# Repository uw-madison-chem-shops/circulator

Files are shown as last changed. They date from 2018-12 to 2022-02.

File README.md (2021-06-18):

# circulator

Circulator for WiHP NMRR. 

coverart

## Repository

This is an open source hardware project licensed under the CERN Open Hardware License Version 2 - Permissive.
Please see the LICENSE file for the complete license.

This repository is being mirrored to several version control systems in an attempt to ensure maximum availability.

| name             | url                                                            |
| ---------------- | -------------------------------------------------------------- |
| Chem             | https://git.chem.wisc.edu/landis-group/WiHP-NMRR/circulator    |
| GitHub (primary) | https://github.com/uw-madison-chem-shops/circulator            |
| GitLab           | https://gitlab.com/uw-madison-chem-shops/circulator            |

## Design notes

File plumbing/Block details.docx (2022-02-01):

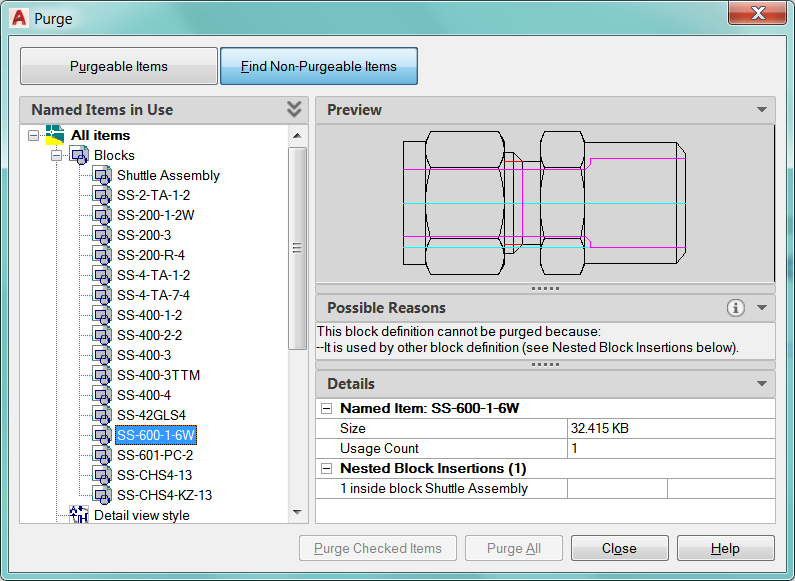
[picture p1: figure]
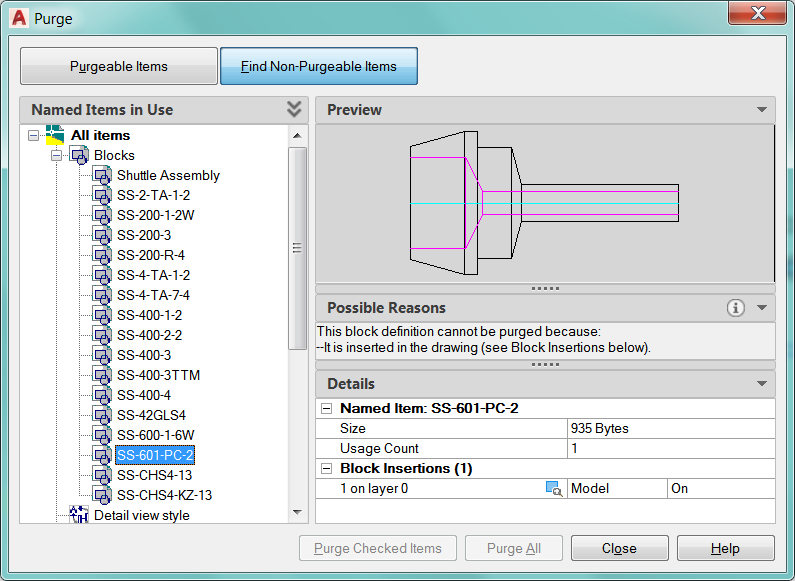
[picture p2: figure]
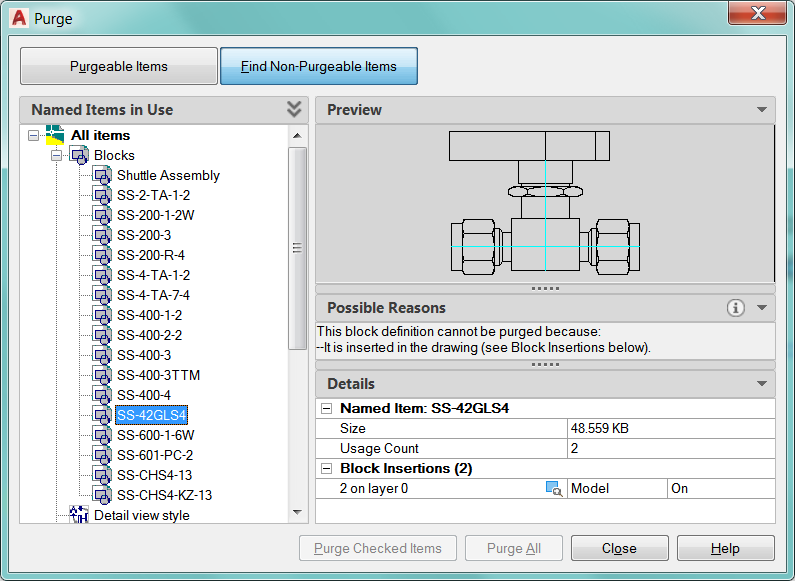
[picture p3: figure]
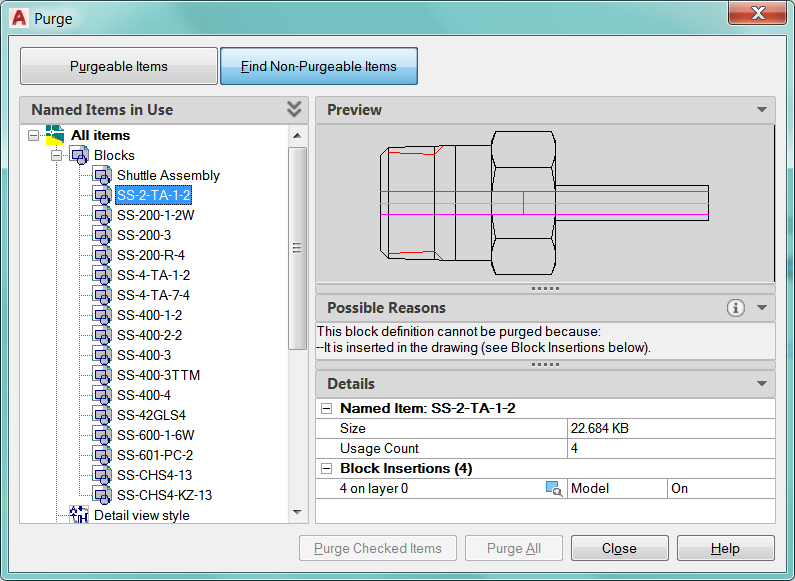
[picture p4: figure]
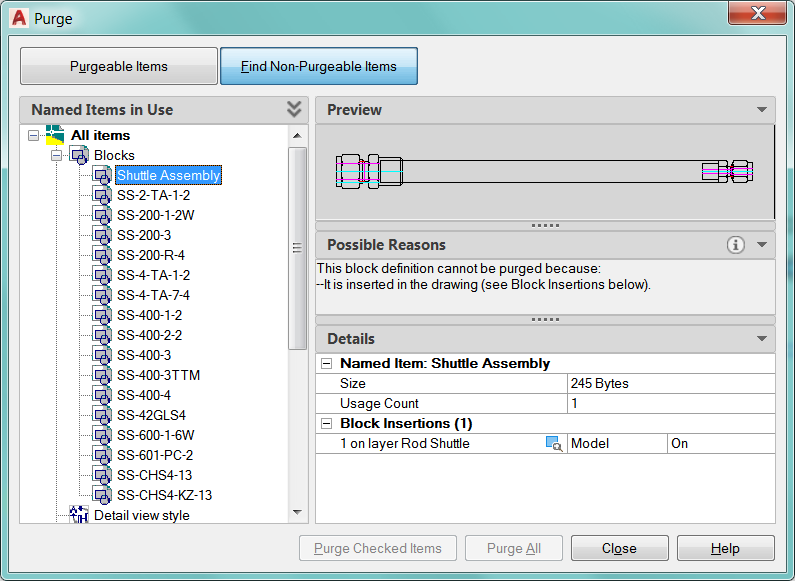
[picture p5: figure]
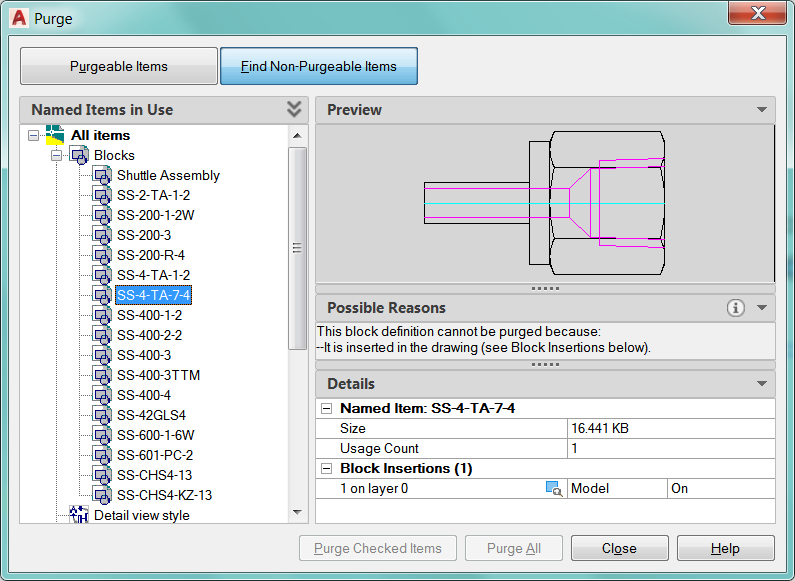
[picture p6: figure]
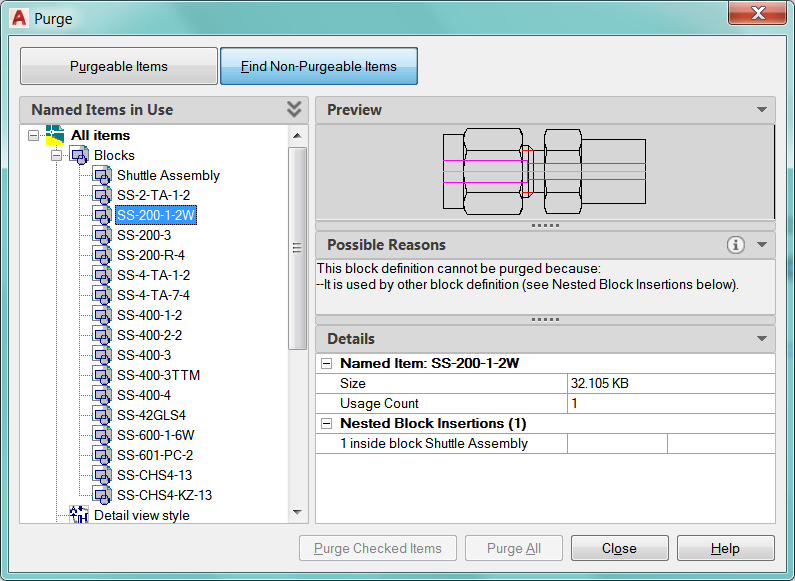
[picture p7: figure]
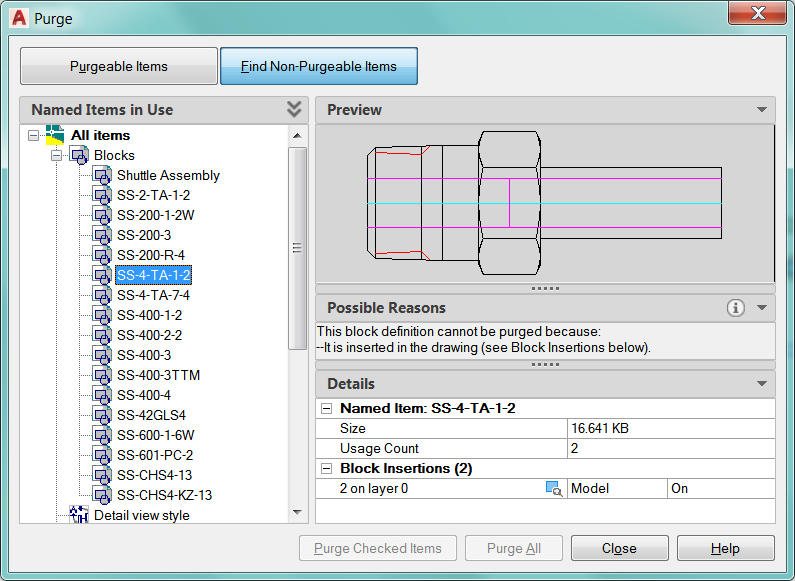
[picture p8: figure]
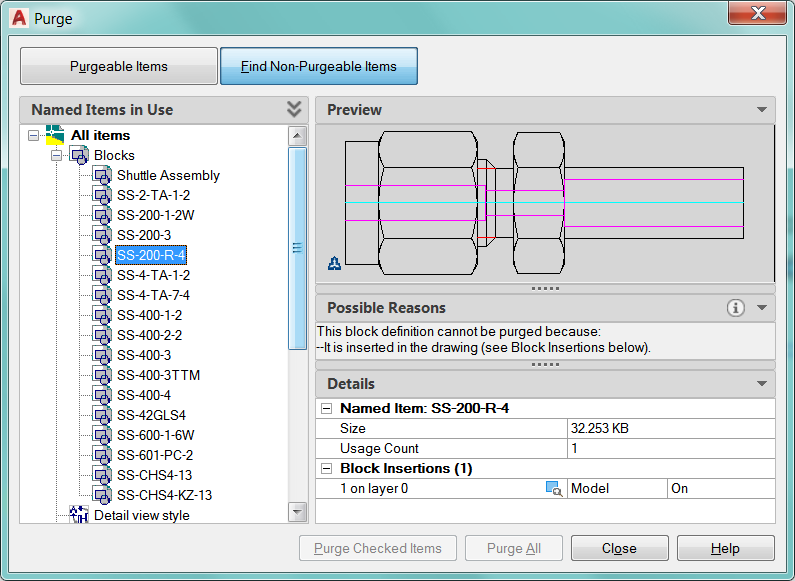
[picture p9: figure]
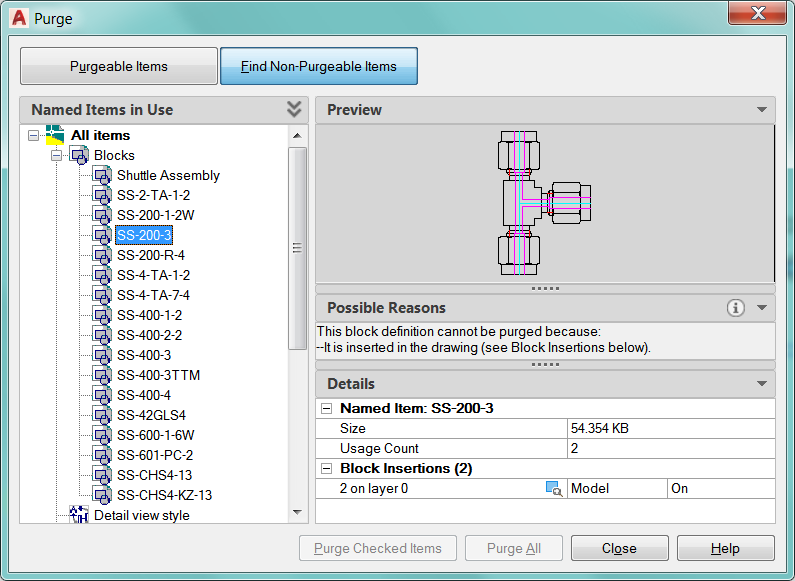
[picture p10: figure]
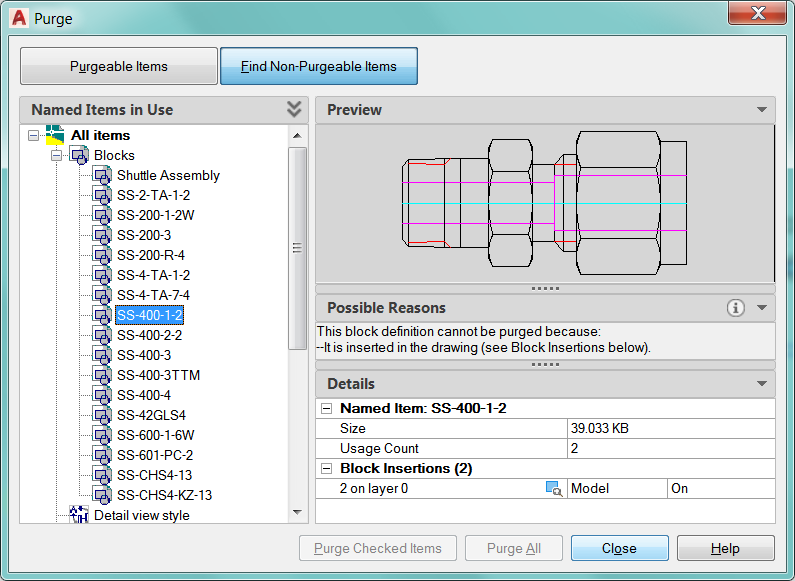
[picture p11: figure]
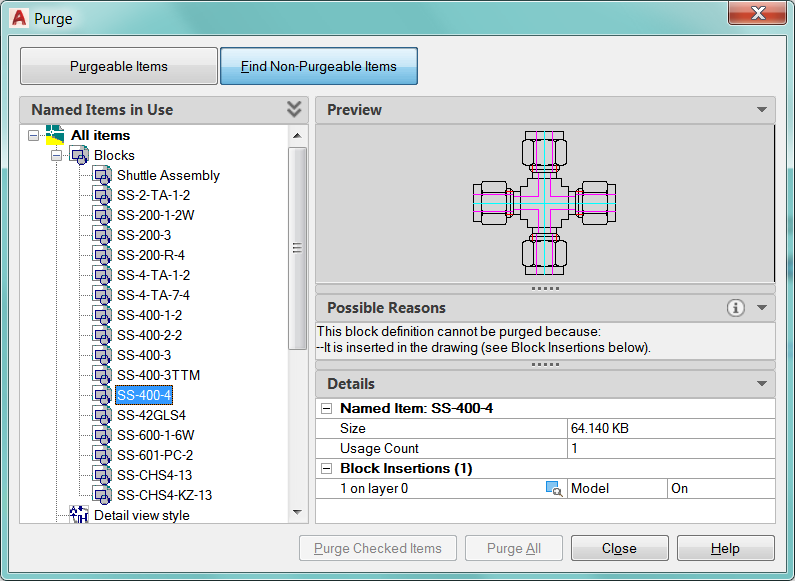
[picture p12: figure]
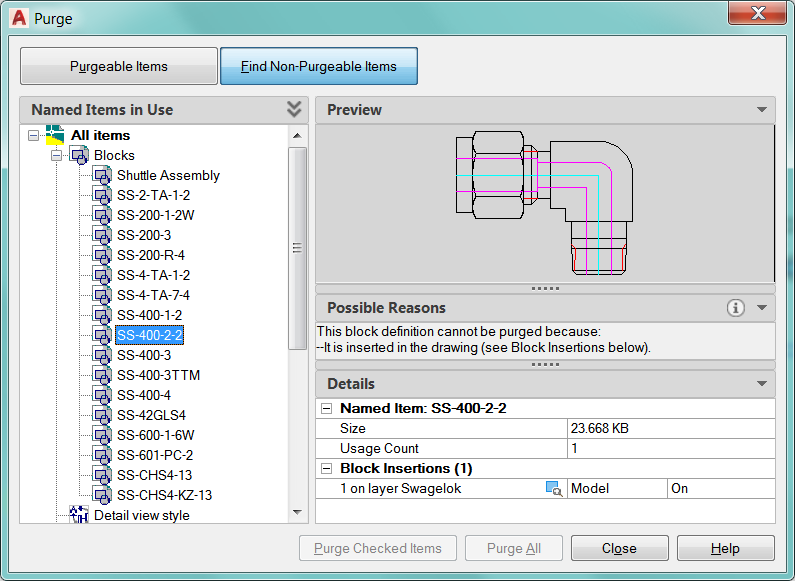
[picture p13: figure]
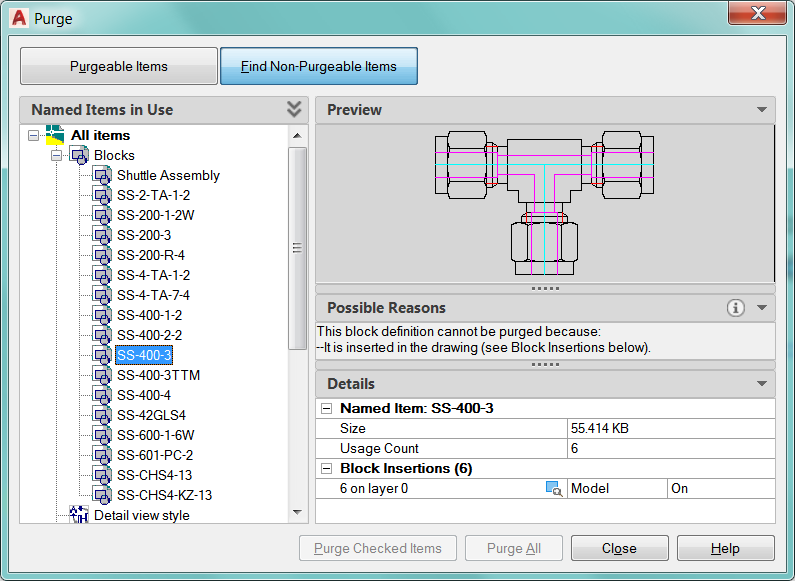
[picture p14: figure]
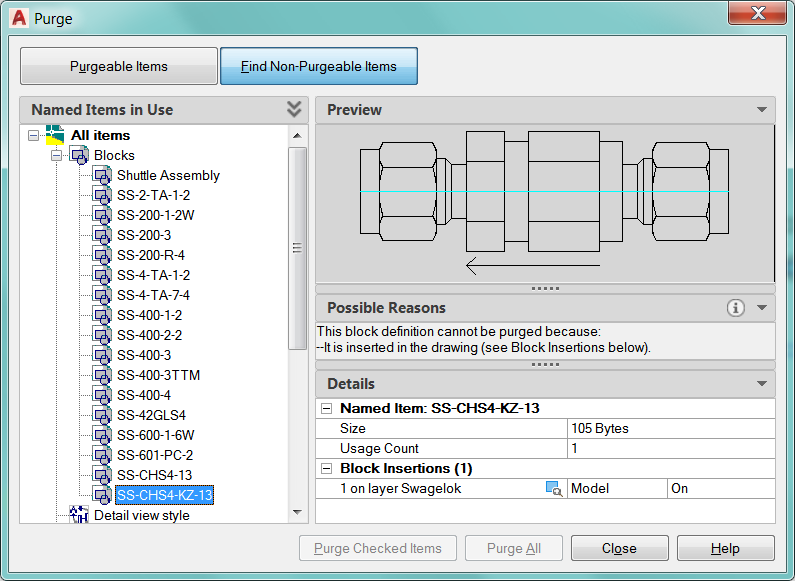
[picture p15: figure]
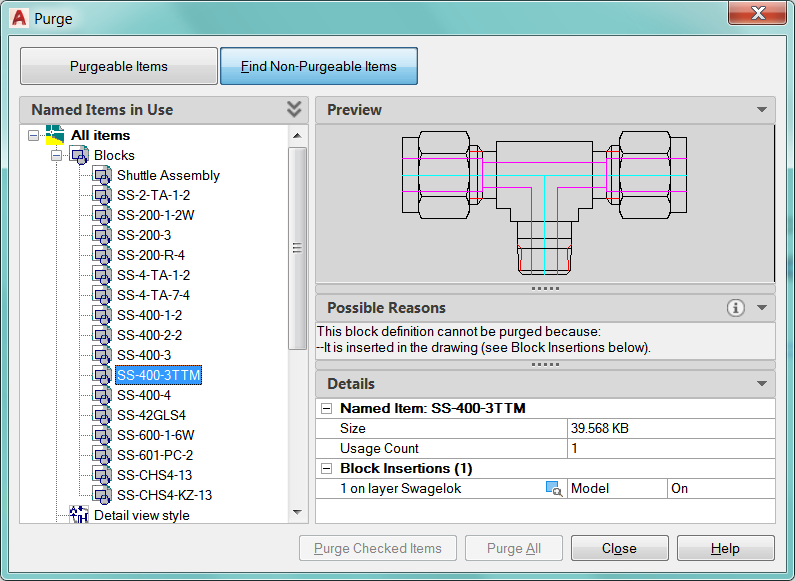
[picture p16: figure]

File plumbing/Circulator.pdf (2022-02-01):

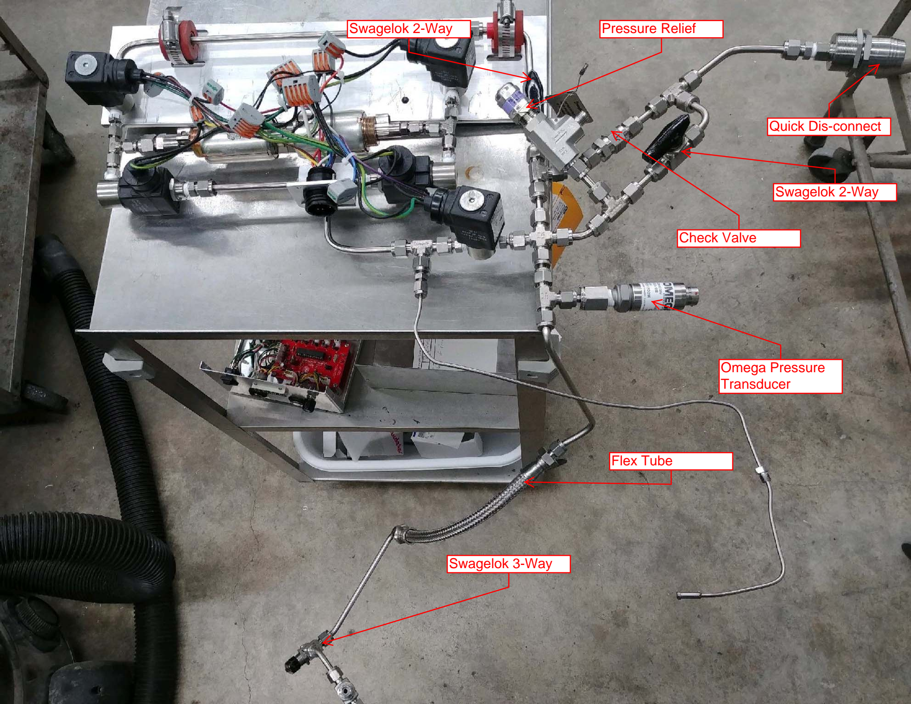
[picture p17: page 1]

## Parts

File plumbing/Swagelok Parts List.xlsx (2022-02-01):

Item | P/N | QTY. | Other
1 | SS-4-TA-7-4 | 1
2 | SS-200-1-2W | 1 | PART OF SHUTTLE
3 | SS-4-TA-1-2 | 2
4 | SHUTTLE ASSY. | 1
5 | SS-600-1-6W | 1 | PART OF SHUTTLE
6 | SS-42GLS4 | 2
7 | SS-601-PC-2 | 1
8 | SS-2-TA-1-2 | 4
9 | SS-200-R-4 | 1
10 | SS-400-1-2 | 2
11 | SS-200-3 | 2
12 | SS-400-4 | 1
13 | SS-400-2-2 | 1
14 | SS-CHS4-KZ-13 | 1
15 | SS-400-3 | 6
16 | SS-400-3TTM | 1

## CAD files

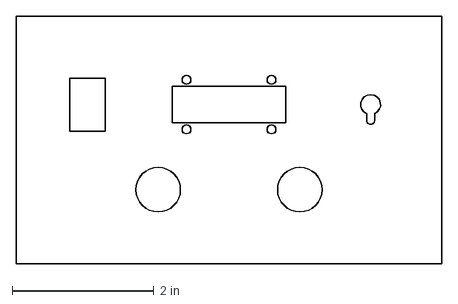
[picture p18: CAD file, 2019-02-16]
enclosure/front.dxf
6.00 x 3.50 in

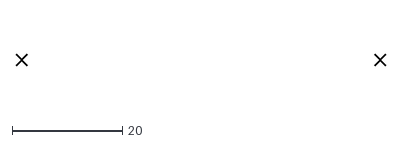
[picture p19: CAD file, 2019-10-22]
literature/power_supply.dxf
67.0 x 2.00

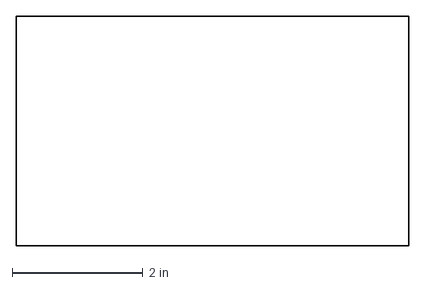
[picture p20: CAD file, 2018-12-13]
enclosure/back.dxf
6.00 x 3.50 in

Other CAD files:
plumbing/Rod Shuttle Assy.dwg
plumbing/Short rod bumper.dwg
plumbing/Circulator_Schem_copy.dwg

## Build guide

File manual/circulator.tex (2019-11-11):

\documentclass{manual}
\pagenumbering{gobble}

\usepackage{listings}

\title{circulator}

\begin{document}

\maketitle

\vspace*{\fill}
\begin{center}
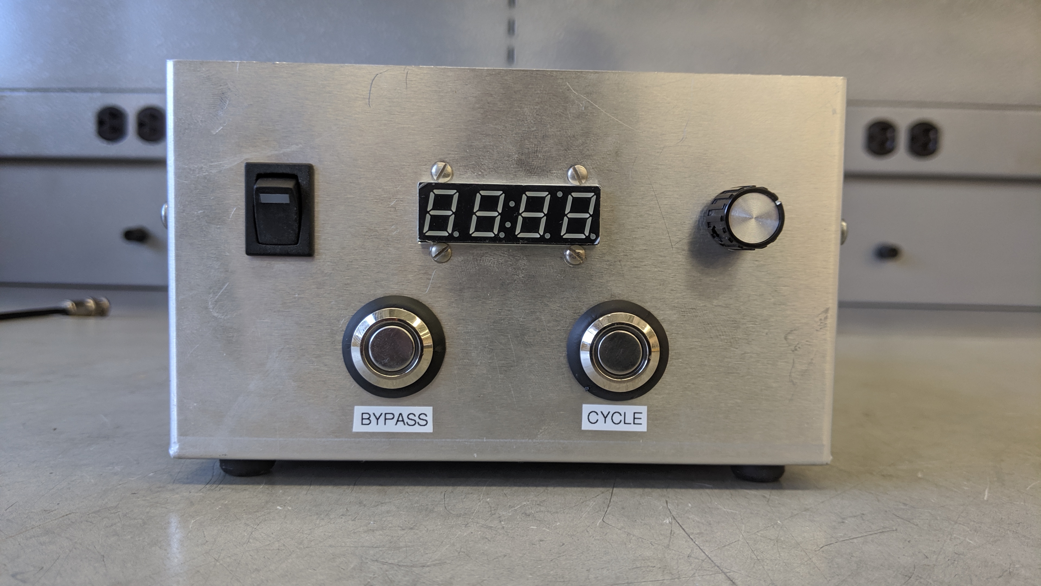
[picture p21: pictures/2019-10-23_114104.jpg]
  
\end{center}
\vspace*{\fill}

\section{description}
\pagenumbering{arabic}

The circulator is responsible for mass transport within the WiHP-NMRR.
It consists of five solenoid valves, and two core solenoids that drive a central piston.
These fire in a certain pattern to drive gas through the WiHP-NMRR.

The circulator driver is an box of electronics that drive the seven solenoids.

\section{solenoids, cable}

\begin{center}
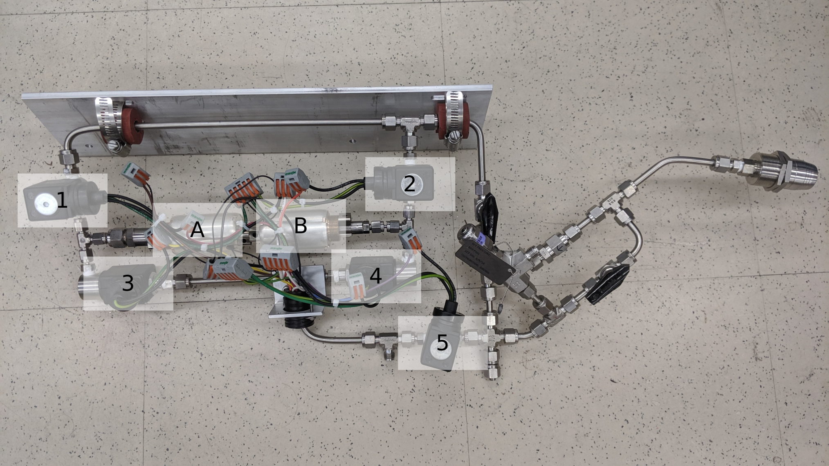
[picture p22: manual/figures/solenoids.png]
  
\end{center}

The image above shows the circulator itself, with the five solenoid valves and two piston solenoids labeled.
The valves are labeled with numbers, one through five.
The piston drivers are labeled with letters, A and B.
This convention is maintained throughout this document.

Valves 1, 2 and 5 are normally closed.
Valves 3 and 4 are normally open.
The following pattern must be followed to circulate:

\begin{table}[h]
\begin{tabular}{l|ll}
  & "tick" & "tock" \\ \hline
A & energized & denergized \\
2 & energized (open) & denergized (closed) \\
4 & energized (closed) & denergized (open) \\
B & denergized & energized \\
1 & denergized (closed) & energized (open) \\
3 & denergized (open) & energized (closed)
\end{tabular}
\end{table}

On the ``tick'' step, the piston moves from B to A, pulling gas through valve 2 and pushing gas out through valve 3.
On the ``tock'' step, the piston moves from A to B, pulling gas through valve 1 and pushing gas out through valve 4.

Valve five bypasses the circulator, and is operated separately from the rest of the solenoids.
The circulator is bypassed when valve five is energized.

\clearpage

Electrically, the five valves all operate on 120 V AC.
The two piston solenoids operate at 12 V DC.
Each of the components has a separate wire controlling line (or positive) voltage within the cable.
The components share ground and neutral.
The piston solenoids are ground referenced.

The circulator is connected by a circular plastic connector, TE/AMP part numbers 206037-1 and 206036-1.
The pin designations are as follows.

\begin{table}[h]
\begin{tabular}{l|ll}
pin & color & assignment \\ \hline
1 & white & neutral \\
2 & red & valve 1 \\
3 & orange & valve 2 \\
4 & yellow & valve 3 \\
5 & blue & valve 4 \\
6 & purple & valve 5 \\
7 & & \\
8 & & \\
9 & & \\
10 & & \\
11 & & \\
12 & & \\
13 & & \\
14 & green & ground \\
15 & brown & solenoid A \\
16 & black & solenoid B
\end{tabular}
\end{table}

\section{electrical box}

\begin{center}
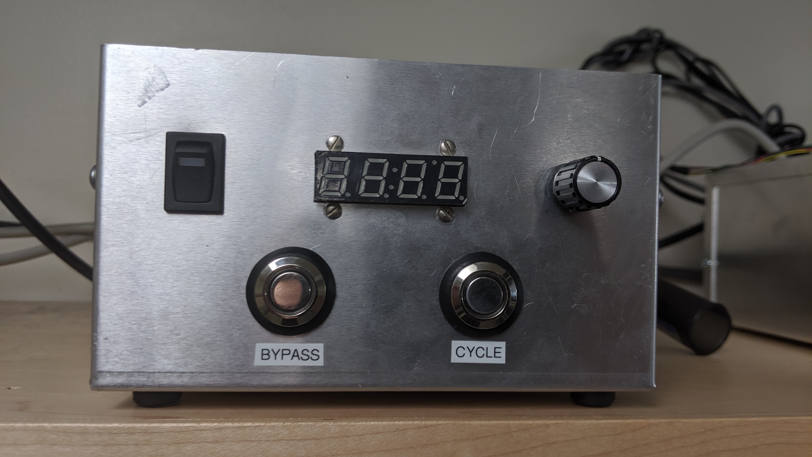
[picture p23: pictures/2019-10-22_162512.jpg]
  
\end{center}

The circulator driver controls the firing of the valves and solenoids necessary for mass transport in the WiHP-NMRR.
The image above is the front of the circulator driver box.
There is a power switch, far left.
The seven segment display in the middle shows the current circulator frequency, in Hz.
This frequency can be adjusted using the encoder knob, right.
Two buttons, one for bypass and the other for cycle, control the current status of the circulator.
Mechanically these are toggle buttons, and each toggles their corresponding state.
Each button contains an illuminated ring which will always display the current state.
These states can also be updated via TTL, as will be discussed later.

\begin{center}
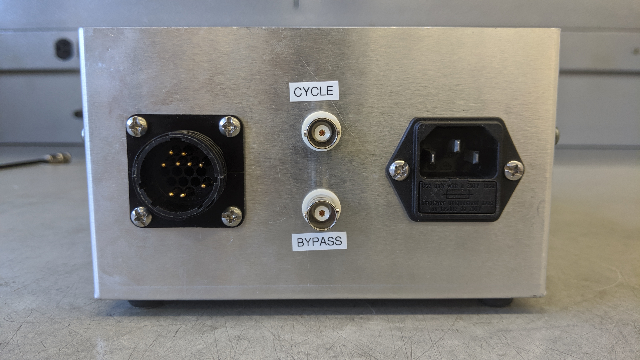
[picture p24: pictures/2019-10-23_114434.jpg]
  
\end{center}

The image above shows the rear of the circulator driver box.
There is a sixteen-pin CPC connector, left, which goes to the circulator itself.
In the middle there are two BNC inputs, cycle and bypass, which accept TTL control from the NMR.
On the right there is power input, which accepts a standard C13 connector.
The circulator operates at 120 V, and may draw up to 5 amps.
There is a fuse within the drawer immediately under the AC entry port.

\clearpage

\begin{center}
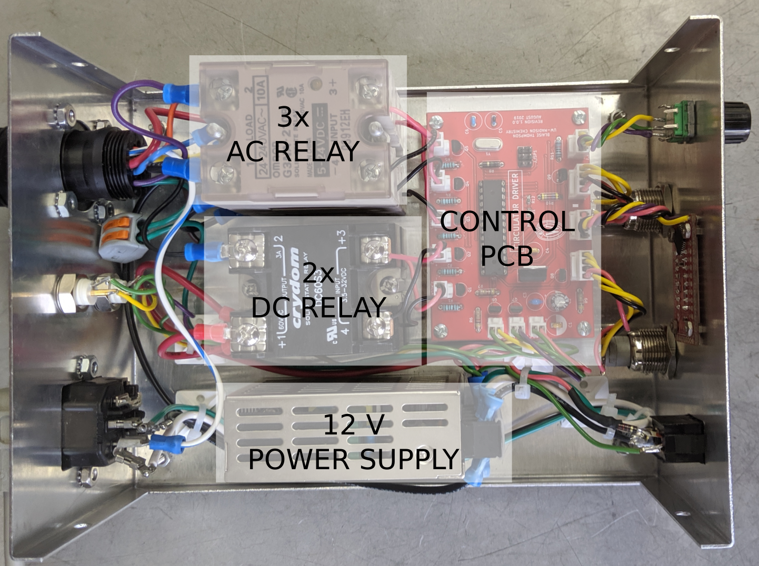
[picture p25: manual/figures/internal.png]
  
\end{center}

The image above shows the internals of the circulator driver box.
The enclosure used is 8'' x 6'' by 3.5'', Bud Industries part number CU-3009-A.
Besides the front and back panel elements, the box contains a 12 V power supply (TRACO part number  TXL 025-12S), 2 DC relays (Crydom part number DC60S3), and 3 AC relays (Omron part number G3NA-205B).
The relays and power supply make up the majority of the cost of the drive electronics.

Also contained within the enclosure is the custom control printed circuit board (PCB).
This central control board accepts power from the 12 V supply, input from the two rear-panel BNC connectors, and connects to the front panel elements and five relays.
At the core of the control board is a microcontroller with custom firmware.
These will all be discussed in the next few sections of this manual.

\section{circuit board}

\begin{center}
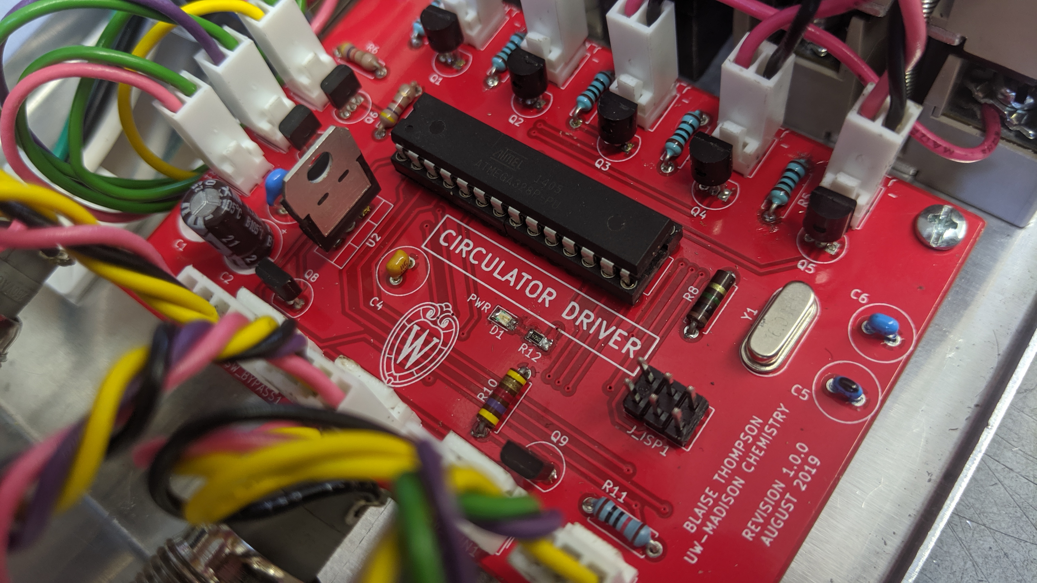
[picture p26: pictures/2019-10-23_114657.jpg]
  
\end{center}

The following pages diagram the printed circuit board (PCB) at the heart of the circulator driver electronics.
This PCB is centered around a single microcontroller, the ATmega328.
A 16 MHz crystal supplies the clock for the microcontroller.
A standard six pin ISP header can be used to program the microcontroller in-circuit.

The microcontroller has outputs to drive five relays, each controlling the action of a small NPN transistor (2N7000) with an appropriate pull-up resistor.
These five relays drive the circulator solenoids, as described in the previous section.
The microcontroller has two TTL inputs, each buffered by a small PNP transistor (BS250) and associated pull-down resistor.

Besides these, the microcontroller has inputs for the two front-panel buttons and the front-panel encoder.
There are also outputs for the LEDs embedded within each front-panel button, and for the seven-segment display (SparkFun part number COM-11441) (driven via I2C).

The following pages contain:
\begin{enumerate}
  \item PCB schematic
  \item PCB silk screen
  \item PCB top copper layer
  \item PCB bottom copper layer
\end{enumerate}
Please note that PCB silk screen and copper representations are to-scale.

The next sections describe the microcontroller firmware and PCB components.

\includepdf[angle=0, fitpaper=true]{../PCB/pcb.pdf}
\includepdf[angle=0, fitpaper=true]{../PCB/silk.pdf}
\includepdf[angle=0, fitpaper=true]{../PCB/front.pdf}
\includepdf[angle=0, fitpaper=true]{../PCB/back.pdf}

\section{firmware}

The following pages contain the raw source-code running on the embedded Atmega328 microcontroller.

\vspace{10pt}
\hrule

\lstinputlisting[language=c++]{../firmware/firmware.ino}

\section{BOM}

The following is an INCOMPLETE bill of materials for the circulator.
Trivial components like screws and resistors have been excluded.

\begin{tabular}{lrrrrl}
item & part & rate & count & total & comment\\
\hline
AC relay & G3NA-205B & 27.00 & 3 & 81.00 & \\
DC relay & DC60S3 & 21.00 & 2 & 42.00 & \\
12 V power supply & TXL 025-12S & 37.00 & 1 & 37.00 & \\
enclosure & CU-3009-A & 16.00 & 1 & 16.00 & \\
CPC pin & 66103-4 & 0.75 & 20 & 15.00 & \\
CPC socket & 1-66105-9 & 0.75 & 20 & 15.00 & \\
CPC plug & 206037-1 & 6.00 & 2 & 12.00 & \\
CPC socket & 206036-1 & 5.00 & 2 & 10.00 & \\
BNC jack & 031-10-RFXG1 & 3.00 & 2 & 6.00 & \\
AC entry & 6200-2300 & 6.00 & 1 & 5.00 & \\
16 MHz xtal & HC-49/U-S16000000ABJB & 1.00 & 1 & 1.00 & \\
header, 2 pin & 22-23-2021 & 0.25 & 8 & 2.00 & \\
header, 4 pin & 22-23-2041 & 0.50 & 3 & 1.50 & \\
header, 3 pin & 22-23-2031 & 0.25 & 1 & 0.25 & \\
DIP socket, 14 pin & 110-93-314-41-0010000 & 1.50 & 2 & 3.00 & \\
housing, 2 pin & 22-01-3027 & 0.25 & 8 & 2.00 & \\
housing, 3 pin & 22-01-3037 & 0.50 & 1 & 0.50 & \\
mosfet, N-channel & 2N7000 & 0.25 & 5 & 1.25 & \\
fuse, 1 A fast &  & 1.00 & 2 & 2.00 & \\
ring terminal, \#6, 14-16 AWG & 34158 & 0.50 & 10 & 5.00 & \\
capacitor, 33 nF & FG14X7R1H334KNT06 & 0.25 & 1 & 0.25 & \\
standoff, 0.5" \#4-40 &  & 0.50 & 4 & 2.00 & \\
housing, 4 pin & 22-01-3047 & 0.50 & 3 & 1.50 & \\
capacitor, 100 uF &  & 0.25 & 1 & 0.25 & \\
regulator, 5 V & 7805 & 1.00 & 1 & 1.00 & \\
switch & R1966ABLKBLKEFGRN & 2.00 & 1 & 2.00 & \\
7 segment display & COM-11441 & 15.00 & 1 & 15.00 & \\
rotary encoder & EN11 & 1.50 & 1 & 1.50 & \\
button, illuminated &  & 2.00 & 2 & 4.00 & \\
terminal block, 2 contact & 222-412 & 0.50 & 8 & 4.00 & \\
terminal block, 3 contact & 222-413 & 0.50 & 2 & 1.00 & \\
terminal block, 5 contact & 222-415 & 0.75 & 3 & 2.25 & \\
rubber bumper & 720 & 0.25 & 4 & 1.00 & \\
\end{tabular}

\end{document}

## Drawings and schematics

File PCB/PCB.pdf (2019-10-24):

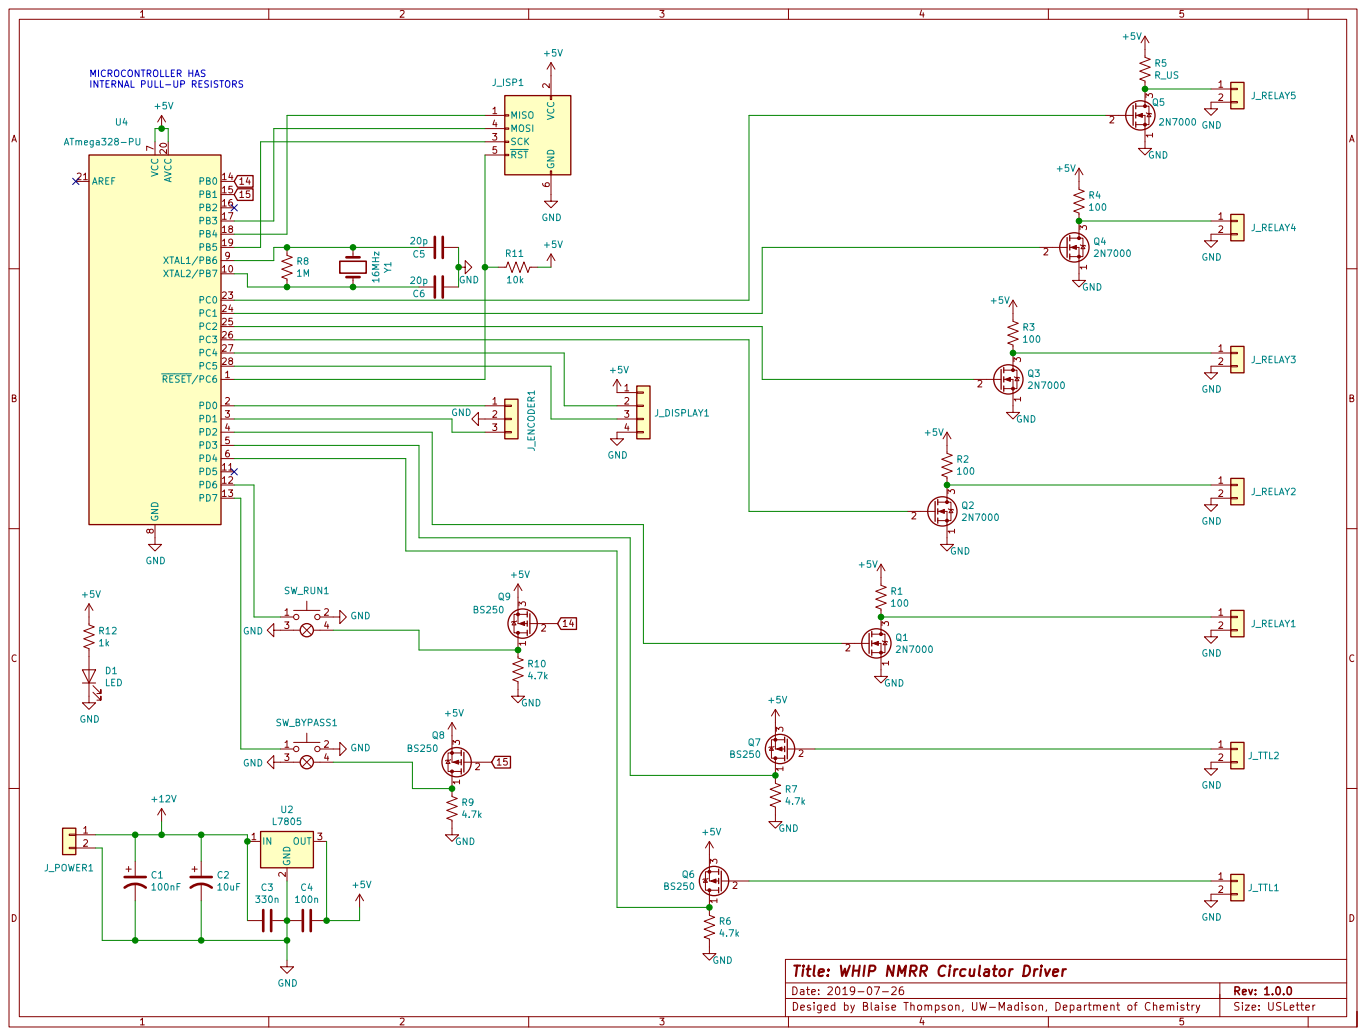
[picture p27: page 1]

14 MICROCONTROLLER HAS
INTERNAL PULL-UP RESISTORS

2 SCK 3 MOSI 4 RST 5 GND

Desiged by Blaise Thompson, UW-Madison, Department of Chemistry

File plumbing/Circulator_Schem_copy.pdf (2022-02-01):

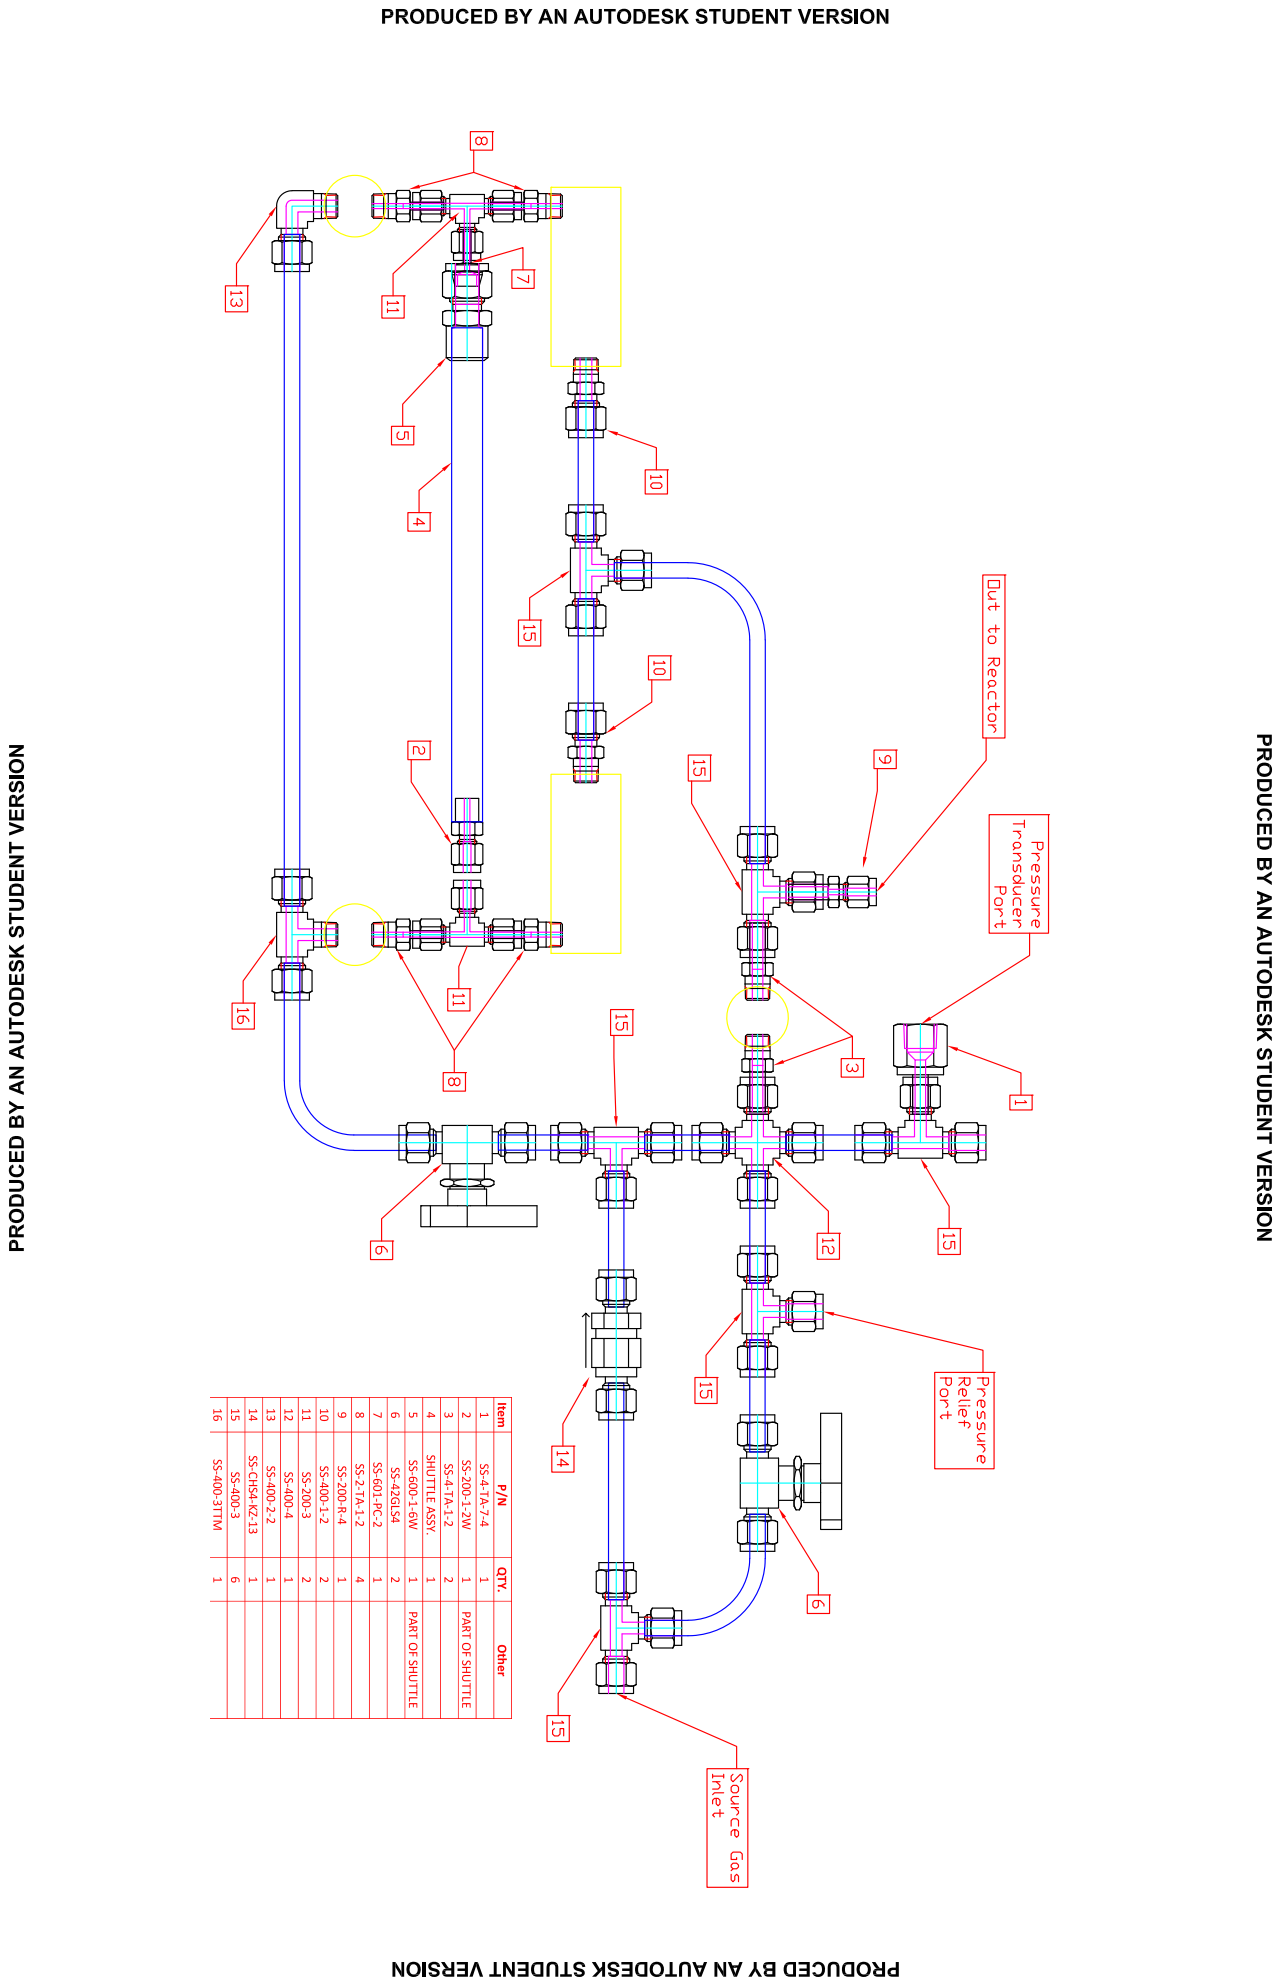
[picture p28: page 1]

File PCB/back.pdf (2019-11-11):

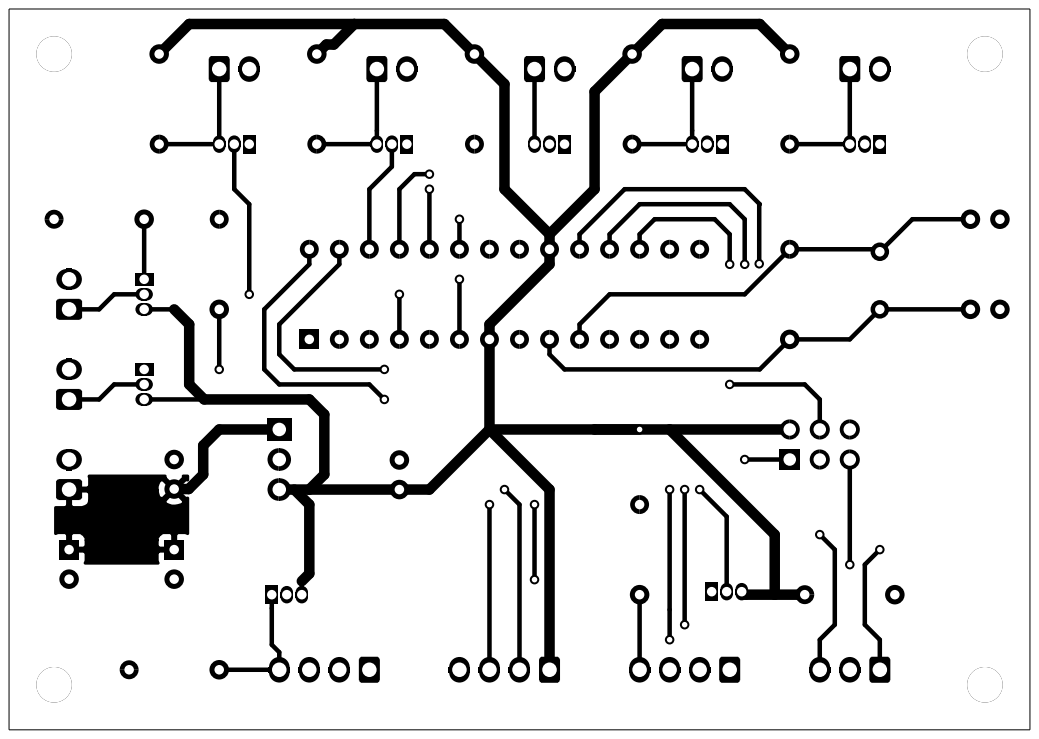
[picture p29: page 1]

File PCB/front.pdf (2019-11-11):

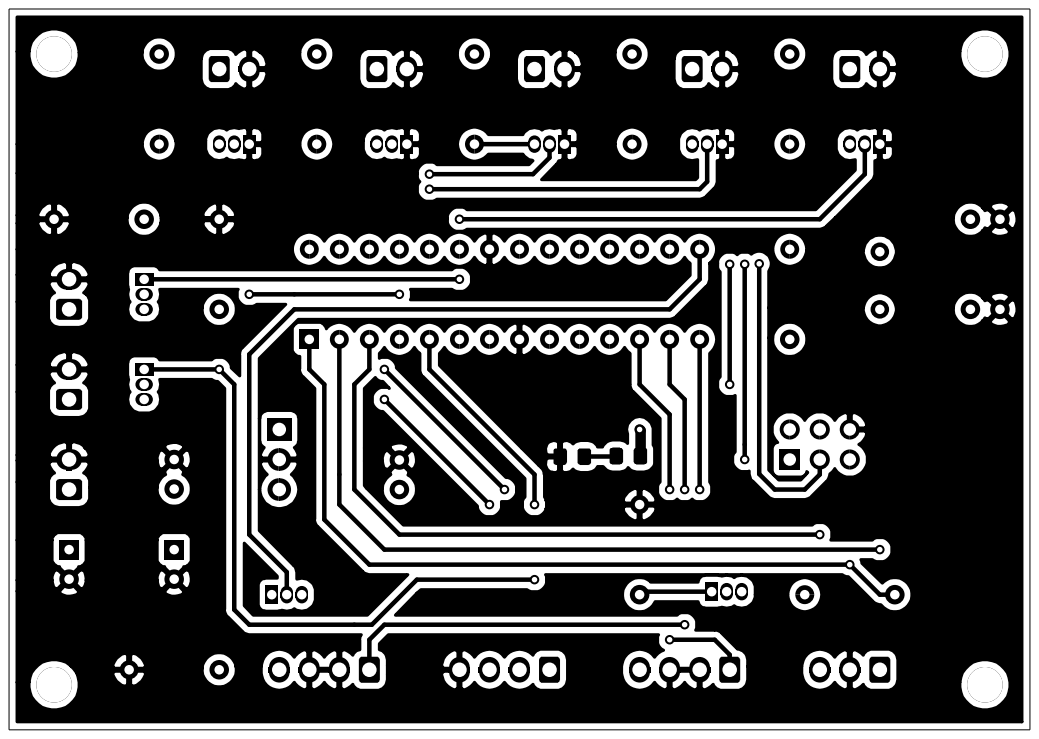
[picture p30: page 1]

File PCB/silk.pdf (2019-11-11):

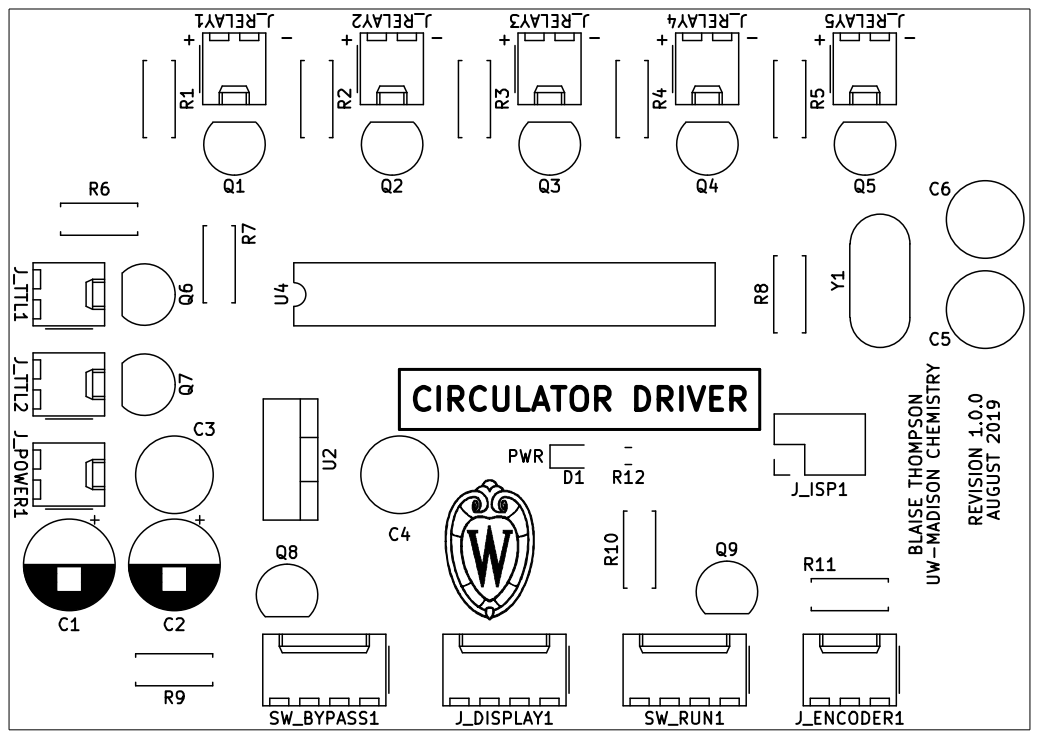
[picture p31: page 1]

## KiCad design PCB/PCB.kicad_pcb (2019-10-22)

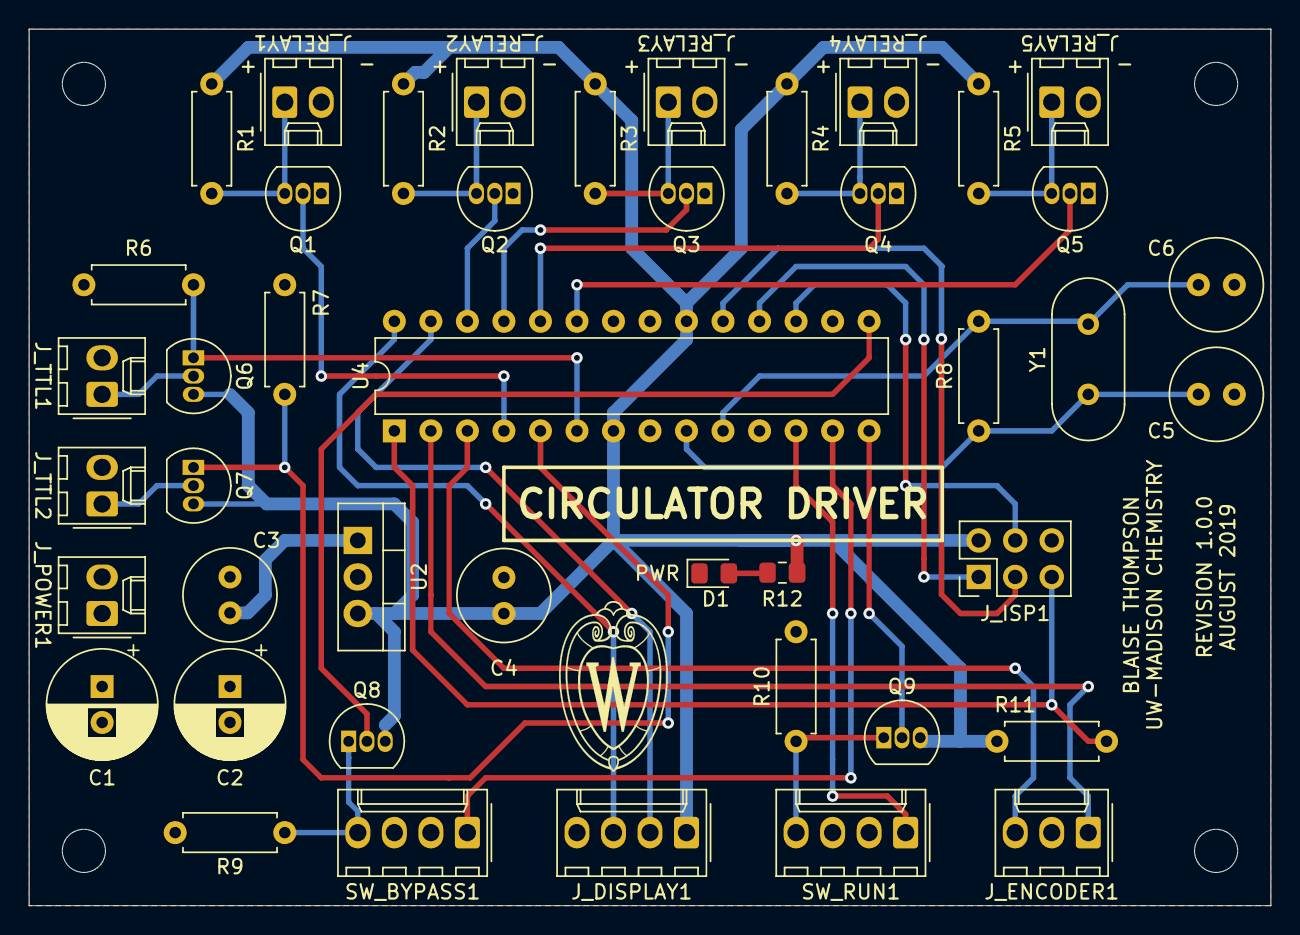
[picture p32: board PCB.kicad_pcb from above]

Board: 2 copper layers, 86.4 x 61.0 mm, 44 parts (0 on the bottom side), 34 nets.

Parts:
C1: 100nF; CP_Radial_D7.5mm_P2.50mm
C2: 10uF; CP_Radial_D7.5mm_P2.50mm
C3: 330n; C_Radial_D6.3mm_H5.0mm_P2.50mm
C4: 100n; C_Radial_D6.3mm_H5.0mm_P2.50mm
C5, C6: 20p; C_Radial_D6.3mm_H5.0mm_P2.50mm
D1: LED; D_0805_2012Metric_Pad1.15x1.40mm_HandSolder
J_DISPLAY1: Conn_01x04; Molex_KK-254_AE-6410-04A_1x04_P2.54mm_Vertical
J_ENCODER1: Conn_01x03; Molex_KK-254_AE-6410-03A_1x03_P2.54mm_Vertical
J_ISP1: AVR-ISP-6; PinHeader_2x03_P2.54mm_Vertical
J_POWER1: Conn_01x02; Molex_KK-254_AE-6410-02A_1x02_P2.54mm_Vertical
J_RELAY1, J_RELAY2, J_RELAY3, J_RELAY4, J_RELAY5: Conn_01x02; Molex_KK-254_AE-6410-02A_1x02_P2.54mm_Vertical
J_TTL1, J_TTL2: Conn_01x02; Molex_KK-254_AE-6410-02A_1x02_P2.54mm_Vertical
Q1, Q2, Q3, Q4, Q5: 2N7000; TO-92_Inline
Q6, Q7, Q8, Q9: BS250; TO-92_Inline
R1, R2, R3, R4, R5, R6, R7, R9, R10: R_US; R_Axial_DIN0207_L6.3mm_D2.5mm_P7.62mm_Horizontal
R8: 1M; R_Axial_DIN0207_L6.3mm_D2.5mm_P7.62mm_Horizontal
R11: 10k; R_Axial_DIN0207_L6.3mm_D2.5mm_P7.62mm_Horizontal
R12: R_US; R_0805_2012Metric_Pad1.15x1.40mm_HandSolder
SW_BYPASS1: SW_Push_Lamp; Molex_KK-254_AE-6410-04A_1x04_P2.54mm_Vertical
SW_RUN1: SW_Push_Lamp; Molex_KK-254_AE-6410-04A_1x04_P2.54mm_Vertical
U2: L7805; TO-220-3_Vertical
U4: ATmega328-PU; DIP-28_W7.62mm
Y1: 16MHz; Crystal_HC49-U_Vertical

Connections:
14: Q9.2, U4.14
15: Q8.2, U4.15
+5V: C4.1, J_DISPLAY1.1, J_ISP1.2, Q6.3, Q7.3, Q8.3, Q9.3, R1.1, R2.1, R3.1, R4.1, R5.1, R11.2, R12.1, U2.3, U4.7, U4.20
+12V: C1.1, C2.1, C3.2, J_POWER1.1, U2.1
GND: C1.2, C2.2, C3.1, C4.2, C5.1, C6.1, D1.1, J_DISPLAY1.4, J_ENCODER1.2, J_ISP1.6, J_POWER1.2, J_RELAY1.2, J_RELAY2.2, J_RELAY3.2, J_RELAY4.2, J_RELAY5.2, J_TTL1.2, J_TTL2.2, Q1.1, Q2.1, Q3.1, Q4.1, Q5.1, R6.2, R7.2, R9.2, R10.2, SW_BYPASS1.2, SW_BYPASS1.3, SW_RUN1.2, SW_RUN1.3, U2.2, U4.8, U4.22
unnamed: C5.2, R8.1, U4.9, Y1.1
unnamed: C6.2, R8.2, U4.10, Y1.2
unnamed: D1.2, R12.2
unnamed: J_DISPLAY1.2, U4.27
unnamed: J_DISPLAY1.3, U4.28
unnamed: J_ENCODER1.1, U4.2
unnamed: J_ENCODER1.3, U4.3
unnamed: J_ISP1.1, U4.18
unnamed: J_ISP1.3, U4.19
unnamed: J_ISP1.4, U4.17
unnamed: J_ISP1.5, R11.1, U4.1
unnamed: J_RELAY1.1, Q1.3, R1.2
unnamed: J_RELAY2.1, Q2.3, R2.2
unnamed: J_RELAY3.1, Q3.3, R3.2
unnamed: J_RELAY4.1, Q4.3, R4.2
unnamed: J_RELAY5.1, Q5.3, R5.2
unnamed: J_TTL1.1, Q6.2
unnamed: J_TTL2.1, Q7.2
unnamed: Q1.2, U4.4
unnamed: Q2.2, U4.26
unnamed: Q3.2, U4.25
unnamed: Q4.2, U4.24
unnamed: Q5.2, U4.23
unnamed: Q6.1, R6.1, U4.6
unnamed: Q7.1, R7.1, U4.5
unnamed: Q8.1, R9.1, SW_BYPASS1.4
unnamed: Q9.1, R10.1, SW_RUN1.4
unnamed: SW_BYPASS1.1, U4.13
unnamed: SW_RUN1.1, U4.12

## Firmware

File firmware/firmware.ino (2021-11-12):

// firmware: circulator-driver

// 7SEG display (I2C communication)
#include <Wire.h> // Include the Arduino SPI library
const byte s7sAddress = 0x71;
char tempString[10];  // used with sprintf to create strings

// rotary encoder
#include <Encoder.h>
Encoder knob(1, 0);  // interrupt, registered in library
long frequency  = 2000;  // mHz

// control pins
int relay1 = 2;  // physical pin 4
int relay2 = A3;  // physical pin 26
int relay3 = A2;  // physical pin 25
int relay4 = A1;  // physical pin 24
int relay5 = A0;  // physical pin 23

// buttons
int bypass_button = 7;  // physical pin 13
int bypass_LED = 9;  // physical pin 15
int run_button = 6;  // physical pin 12
int run_LED = 8;  // physical pin 14

// TTL
int TTL1 = 4;  // physical pin 6
int TTL1_state = HIGH;
int TTL2 = 3;  // physical pin 5
int TTL2_state = HIGH;

// run control
bool bypass_state = LOW;
bool run_state = LOW;

// timing control
bool state = LOW;
float period = 1e6;               // interval at which to blink (milliseconds)
unsigned long previousMillis = 0;        // will store last time LED was updated

void setup()
{
  // 7SEG display (I2C communication)
  Wire.begin();  // Initialize hardware I2C pins
  clearDisplayI2C();  // Clears display, resets cursor
  s7sSendStringI2C("-HI-");
  setDecimalsI2C(0b111111);  // Turn on all decimals, colon, apos
  setBrightnessI2C(255);  // 0 to 255
  clearDisplayI2C();
  setDecimalsI2C(0b00000010);
  sprintf(tempString, "%04d", frequency / 10);
  s7sSendStringI2C(tempString);
  // rotary encoder
  knob.write(0);
  // serial
  Serial.begin(9600);
  // output pins
  pinMode(relay1, OUTPUT);
  pinMode(relay2, OUTPUT);
  pinMode(relay3, OUTPUT);
  pinMode(relay4, OUTPUT);
  pinMode(relay5, OUTPUT);
  pinMode(bypass_LED, OUTPUT);
  pinMode(run_LED, OUTPUT);
  // input pins
  pinMode(bypass_button, INPUT_PULLUP);
  pinMode(run_button, INPUT_PULLUP);
  pinMode(TTL1, INPUT_PULLUP);
  pinMode(TTL2, INPUT_PULLUP);
  //
  period = 1e6 / (float)frequency;
  delay(1000);
}

void loop() {
  // buttons (active low)
  if (digitalRead(bypass_button) == LOW) {
    while (digitalRead(bypass_button) == LOW) {
      delay(1);  // ms
    }
    bypass_state = !bypass_state;
  }
  digitalWrite(bypass_LED, !bypass_state);  // active low
  if (digitalRead(run_button) == LOW) {
    while (digitalRead(run_button) == LOW) {
      delay(1);  // ms
    }
    run_state = !run_state;
  }
  // TTL
  int ttl1 = digitalRead(TTL1);
  if (ttl1 != TTL1_state) {
    TTL1_state = ttl1;
    run_state = !ttl1;
  }
  int ttl2 = digitalRead(TTL2);
  if (ttl2 != TTL2_state) {
    TTL2_state = ttl2;
    bypass_state = !ttl2;
    run_state = ttl2;
  }
  digitalWrite(run_LED, !run_state);  // active low
  // input from rotary encoder
  int x = knob.read();
  int sign = (x > 0) - (x < 0);
  if (abs(x) >= 4) {
    if (frequency == 25000) {
      if (sign == -1) {
        frequency -= 1000;
      }
    }
    else if (10000 < frequency) {
      frequency += 1000 * sign;
    }
    else if (frequency == 10000) {
      if (sign == 1) frequency += 1000;
      if (sign == -1) frequency -= 100;
    }
    else if ((1000 < frequency) && (frequency < 10000)) {
      frequency += 100 * sign;
    }
    else if (frequency == 1000) {
      if (sign == 1) frequency += 100;
      if (sign == -1) frequency -= 10;
    }
    else if ((20 <= frequency) && (frequency < 1000)) {
      frequency += 10 * sign;
    }
    else {
      if (sign == 1) {
        frequency += 10;
      }
    }
    sprintf(tempString, "%04d", frequency / 10);
    s7sSendStringI2C(tempString);
    knob.write(0);
    period = 1e6 / (float)frequency;
  }
  // control cycle relays
  unsigned long currentMillis = millis();
  if (currentMillis - previousMillis >= (period / 2)) {
    previousMillis = currentMillis;
    if (run_state == HIGH) {
      state = !state;
    }
    digitalWrite(relay1, state);  // A
    digitalWrite(relay4, state);  // 2, 4
    digitalWrite(relay2, !state);  // B
    digitalWrite(relay3, !state);  // 1, 3
  }
  // control bypass relay
  digitalWrite(relay5, !bypass_state);  // low active
}

void s7sSendStringI2C(String toSend) {
  // This custom function works somewhat like a serial.print.
  //  You can send it an array of chars (string) and it'll print
  //  the first 4 characters in the array.
  Wire.beginTransmission(s7sAddress);
  for (int i = 0; i < 4; i++) {
    Wire.write(toSend[i]);
  }
  Wire.endTransmission();
}

void clearDisplayI2C() {
  // Send the clear display command (0x76)
  //  This will clear the display and reset the cursor
  Wire.beginTransmission(s7sAddress);
  Wire.write(0x76);  // Clear display command
  Wire.endTransmission();
}

void setBrightnessI2C(byte value) {
  // Set the displays brightness. Should receive byte with the value
  //  to set the brightness to
  //  dimmest------------->brightest
  //     0--------127--------255
  Wire.beginTransmission(s7sAddress);
  Wire.write(0x7A);  // Set brightness command byte
  Wire.write(value);  // brightness data byte
  Wire.endTransmission();
}

void setDecimalsI2C(byte decimals) {
  // Turn on any, none, or all of the decimals.
  //  The six lowest bits in the decimals parameter sets a decimal
  //  (or colon, or apostrophe) on or off. A 1 indicates on, 0 off.
  //  [MSB] (X)(X)(Apos)(Colon)(Digit 4)(Digit 3)(Digit2)(Digit1)
  Wire.beginTransmission(s7sAddress);
  Wire.write(0x77);
  Wire.write(decimals);
  Wire.endTransmission();
}
